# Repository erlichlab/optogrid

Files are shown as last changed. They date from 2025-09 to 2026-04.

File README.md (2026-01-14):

# OptoGrid

OptoGrid is a battery-powered BLE-enabled low-cost wireless random access optogenetic stimulation device, with 9-axis (acceleration XYZ, angular veleocity XYZ, magnetic field XYZ) movement tracking capability. 

## Specification

### Weight
| Component                | Weight (g) |
|--------------------------|------------|
| Battery PCB Assembly     | 0.9        |
| Main PCB Assembly        | 0.5        |
| Housing units + magnets  | 1.0        |
| **Total weight**         | **2.4**    |

### Battery link
https://www.aliexpress.com/item/1005007806295703.html?spm=a2g0o.order_list.order_list_main.10.24551802WD2qNq

## Folder Structure

- **3D/**  
  CAD models and mechanical assemblies for OptoGrid.

- **PCB/**  
  Original PCB project file (.eprj) exported from JLCEDA Pro, a folder containing PCB design files exported to Altium Designer format, PDF of the schematics, and exported PCBA production files.
- **OptoGrid_Photos.pdf/**  
  Photos of OptoGrid V0.05 assembly.
- **Assembly_SOP_V1.pdf/**  
  Protocl to reproduce OptoGrid V0.05 assembly.

## Purpose

This repository is to share the hardware design files of OptoGrid with OpenEphys. Its license is set to "All Rights Reserved" for now until device distribution begins.

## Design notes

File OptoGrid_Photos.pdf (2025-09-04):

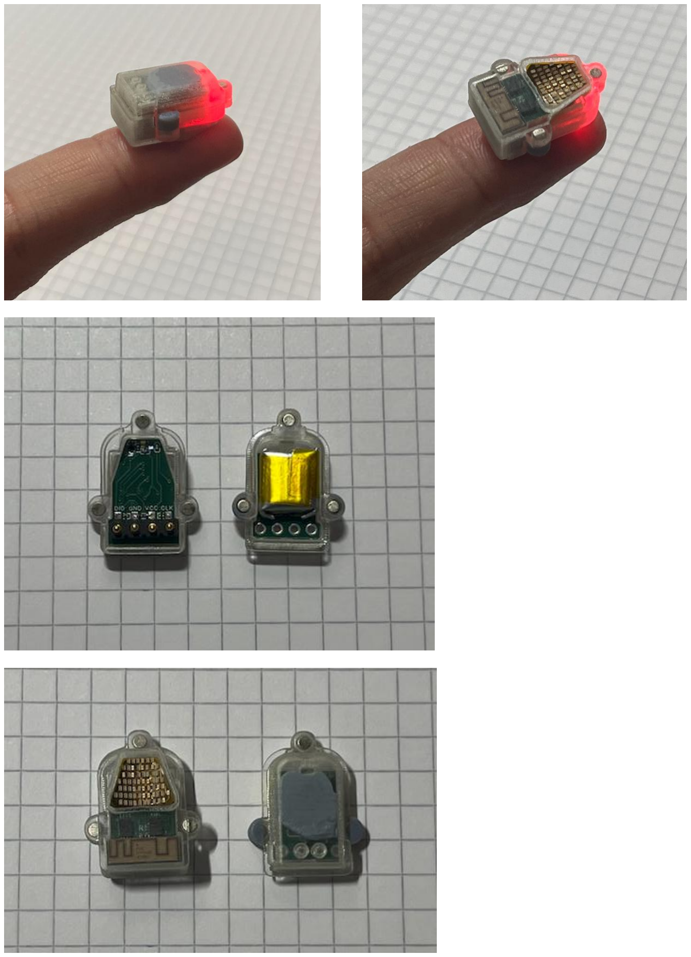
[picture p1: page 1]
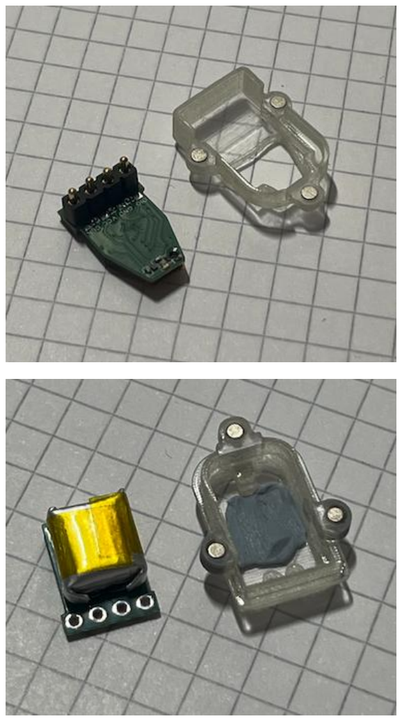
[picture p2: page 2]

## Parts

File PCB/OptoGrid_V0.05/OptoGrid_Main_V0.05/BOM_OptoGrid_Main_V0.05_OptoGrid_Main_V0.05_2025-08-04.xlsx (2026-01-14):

No. | Quantity | Comment | Designator | Footprint | Value | Manufacturer Part | Manufacturer | Supplier Part | Supplier | Name
1 | 2 | 2.2uF | C46,C54 | C0201 | 2.2uF | GRM033R61A225KE47D | muRata(村田) | C335106 | LCSC | 2.2uF
2 | 4 | Test-Point | CLK,DIO,GND,VCC | Test-Point-0.5mm
3 | 1 | YXT-BB10-16S-02 | CN1 | CONN-SMD_YXT-BB10-16S-02 |  | YXT-BB10-16S-02 | YXT(益鑫通） | C2763964 | LCSC | YXT-BB10-16S-02
4 | 1 | 811-22-004-30-002101 | J1 | 811-22-004-30-002101 |  | 811-22-004-30-002101 | Mill-Max | C29643123 | LC
5 | 1 | 220Ω | R2 | R0201 | 220Ω | RC0201FR-07220RL | YAGEO(国巨) | C274342 | LCSC | 220Ω
6 | 2 | 4.7kΩ | R4,R9 | R0201 | 4.7kΩ | AF0201FR-074K7L | YAGEO(国巨) | C2105831 | LCSC | 4.7kΩ
7 | 1 | 71.5Ω | R5 | R0201 | 71.5Ω | 0201WMF715JTEE | UNI-ROYAL(厚声) | C423441 | LCSC | 71.5Ω
8 | 1 | 82Ω | R6 | R0201 | 82Ω | RC-01W82R0FT | FH | C321062 | LCSC | 82Ω
9 | 2 | 1MΩ | R7,R8 | R0201 | 1MΩ | RC0201FR-071ML | YAGEO(国巨) | C295786 | LCSC | 1MΩ
10 | 1 | RED LED | U3 | BLUE_LED_KINGBRIGHT_0201 |  | APG0603SURC-TT | Kingbright | C5356830 | LCSC | RED LED
11 | 1 | HY0020 | U5 | HY0020_footprint_NoFilling
12 | 2 | TMUX1208RSVR | U6,U11 | UTQFN-16_L2.6-W1.8-P0.40-BL |  | TMUX1208RSVR | TI(德州仪器) | C2673274 | LCSC | TMUX1208RSVR
13 | 1 | NCP163AFCT330T2G | U7 | WLCSP-4_L0.6-W0.6-P0.35-R2-C2-TL |  | NCP163AFCT330T2G | onsemi(安森美) | C603648 | LCSC | NCP163AFCT330T2G
14 | 1 | BLUE LED | U12 | BLUE_LED_KINGBRIGHT_0201 |  | APG0603VBC-A1-5MAV | Kingbright | C5846953 | LCSC | BLUE LED

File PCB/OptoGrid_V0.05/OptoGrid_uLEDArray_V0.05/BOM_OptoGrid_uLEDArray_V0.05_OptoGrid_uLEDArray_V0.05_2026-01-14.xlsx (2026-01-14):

No. | Quantity | Comment | Designator | Footprint | Value | Manufacturer Part | Manufacturer | Supplier Part | Supplier | Name
1 | 1 | YXT-BB10-16P-02 | CN1 | CONN-SMD_YXT-BB10-16P-02 |  | YXT-BB10-16P-02 | YXT(益鑫通） | C2763972 | LCSC | YXT-BB10-16P-02
2 | 64 | BLUE LED | U1,U29,U30,U31,U32,U33,U34,U35,U36,U38,U39,U40,U41,U42,U43,U44,U45,U47,U48,U49,U50,U51,U52,U53,U54,U56,U57,U58,U59,U60,U61,U62,U63,U66,U67,U68,U69,U70,U71,U72,U73,U74,U75,U76,U77,U78,U79,U80,U81,U83,U84,U85,U86,U87,U88,U89,U90,U92,U93,U94,U96,U97,U98,U99 | BLUE_LED_KINGBRIGHT_0201 |  | XL-0201UBC (Brightness Grading D5) | XINGLIGHT | C3646921 | LCSC | BLUE LED

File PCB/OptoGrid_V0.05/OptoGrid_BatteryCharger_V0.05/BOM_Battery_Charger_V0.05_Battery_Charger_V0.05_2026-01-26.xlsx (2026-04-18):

No. | Quantity | Comment | Designator | Footprint | Value | Manufacturer Part | Manufacturer | Supplier Part | Supplier | Name
1 | 12 | 10uF | C1,C2,C3,C4,C5,C6,C7,C8,C9,C10,C11,C12 | C0603 | 10uF | CL10A106MA8NRNC | SAMSUNG(三星) | C96446 | LCSC | 10uF
2 | 6 | 811-22-002-30-001101 | J7,J8,J9,J10,J11,J12 | MilMax_2Pin_2.54mmPitch_4.49mmTall_SMT |  |  |  |  |  | 811-22-002-30-001101
3 | 6 | 44.2kΩ | R2,R27,R28,R29,R30,R31 | R0603 | 44.2kΩ | 0603WAF4422T5E | UNI-ROYAL(厚声) | C23056 | LCSC | 44.2kΩ
4 | 6 | 1kΩ | R3,R7,R10,R13,R16,R19 | R0603 | 1kΩ | 0603WAF1001T5E | UNI-ROYAL(厚声) | C21190 | LCSC | 1kΩ
5 | 2 | 5.1kΩ | R4,R5 | R0603 | 5.1kΩ | 0603WAF5101T5E | UNI-ROYAL(厚声) | C23186 | LCSC | 5.1kΩ
6 | 6 | 2kΩ | R21,R22,R23,R24,R25,R26 | R0603 | 2kΩ | 0603WAF2001T5E | UNI-ROYAL(厚声) | C22975 | LCSC | 2kΩ
7 | 6 | TP4056-MS | U1,U3,U5,U7,U9,U11 | SOP-8_L4.9-W3.9-P1.27-LS6.0-TL-EP |  | TP4056-MS | MSKSEMI(美森科) | C7473158 | LCSC | TP4056-MS
8 | 6 | XL-1608SURUGC | U2,U4,U6,U8,U10,U12 | LED-SMD_4P-L1.6-W0.8-RD_1 |  | XL-1608SURUGC | XINGLIGHT(成兴光) | C5349934 | LCSC | XL-1608SURUGC
9 | 2 | TYPE-C 6P(073) | USB1,USB2 | TYPE-C-SMD_TYPE-C-6P_5 |  | TYPE-C 6P(073) | SHOU HAN(首韩) | C668623 | LCSC | TYPE-C 6P(073)

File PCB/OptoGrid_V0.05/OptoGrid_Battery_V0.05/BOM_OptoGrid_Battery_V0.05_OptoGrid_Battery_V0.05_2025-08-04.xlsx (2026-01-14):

No. | Quantity | Comment | Designator | Footprint | Value | Manufacturer Part | Manufacturer | Supplier Part | Supplier | Name
1 | 3 | 2.2uF | C46,C48,C54 | C0201 | 2.2uF | GRM033R61A225KE47D | muRata(村田) | C335106 | LCSC | 2.2uF
2 | 1 | 10nF | C49 | C0201 | 10nF | GRM033R71A103KA01D | muRata(村田) | C76941 | LCSC | 10nF
3 | 1 | 100nF | C50 | C0201 | 100nF | GRM033Z71A104KE14D | muRata(村田) | C161494 | LCSC | 100nF
4 | 1 | 100nF | C55 | C0201 | 100nF | GRM033R61E104KE14D | muRata(村田) | C76939 | LCSC | 100nF
5 | 1 | 10uF | C57 | C0402 | 10uF | CL05A106MP5NUNC | SAMSUNG(三星) | C315248 | LCSC | 10uF
6 | 1 | 220nF | C60 | C0201 | 220nF | GRM033R61E224KE01D | muRata(村田) | C701263 | LCSC | 220nF
7 | 1 | 2.2uF | C61 | C0402 | 2.2uF | GRM155Z71A225KE01D | muRata(村田) | C2997286 | LCSC | 2.2uF
8 | 1 | BAT30F4 | D1 | DFN0603-D_L0.6-W0.3-P0.34-RD |  | BAT30F4 | ST(意法半导体) | C314018 | LCSC | BAT30F4
9 | 1 | 510Ω | R3 | R0201 | 510Ω | RC0201FR-07510RL | YAGEO(国巨) | C57784 | LCSC | 510Ω
10 | 1 | DS6101AED4 | U2 | DFN-4_L1.0-W1.0-P0.65-BL-EP |  | DS6101AED4 | DSTECH(奥简科技) | C7499469 | LCSC | DS6101AED4
11 | 1 | NCP163AFCT330T2G | U7 | WLCSP-4_L0.6-W0.6-P0.35-R2-C2-TL |  | NCP163AFCT330T2G | onsemi(安森美) | C603648 | LCSC | NCP163AFCT330T2G
12 | 1 | LIS2MDLTR | U8 | LGA-12_L2.0-W2.0-P0.50-BL |  | LIS2MDLTR | ST(意法半导体) | C919695 | LCSC | LIS2MDLTR
13 | 1 | IIM-42652 | U9 | LGA-14_L3.0-W2.5-P0.50-TL |  | IIM-42652 | TDK InvenSense(应美盛) | C2988404 | LCSC | IIM-42652

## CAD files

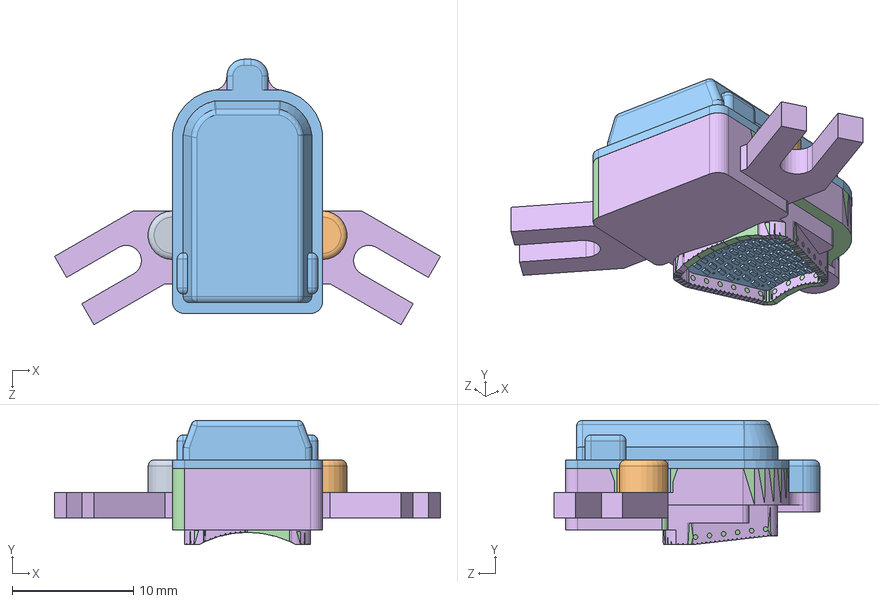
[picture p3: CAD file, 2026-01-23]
3D/OptoGrid_V0.051_Assembly.STEP
31.8 x 10.2 x 21.9 mm
2-UpperHousing_OptoGrid_V0.05_Battery
1-OptoGrid_LowerHousing_no_headfix
COMPOUND_2.step x 2
COMPOUND-0_2.step
COMPOUND-1_2.step x 7
COMPOUND-2_2.step
pPdb-Board.step
pPdb-U6-UTQFN-16_L2.6-W1.8-P0.40-BL.step x 2
B-Flex_uLEDMatrix
BOT_Mold_V0.04
HY0020
1B-OptoGrid_LowerHousing_headfix
Magnet_2mm1mm x 3
COMPOUND_1.step
COMPOUND-0_1.step
COMPOUND-1_1.step x 7
COMPOUND-2_1.step
COMPOUND-3_1.step
vdLQ-Board.step
vdLQ-U2-DFN-4_L1.0-W1.0-P0.65-BL-EP.step
vdLQ-C57-C0402.step x 2
vdLQ-D1-DFN0603-D_L0.6-W0.3-P0.34-RD.step
Battery_25mAh
Magnet_2mm2mm x 3

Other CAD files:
3D/OptoGrid_V0.051_Assembly.SLDASM

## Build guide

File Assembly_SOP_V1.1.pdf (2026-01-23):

## Procedure to assemble the OptoGrid device

Ver. | Author | Date | Note
1.0 | Fukui (Daniel) Yang, Sainsbury Wellcome Centre, UCL | 14/01/2026 | Initial Commit
1.1 | Fukui (Daniel) Yang | 23/01/2026 | Changed 3D model for head-fixed base plate; magnets from N42 to N52

## Table of content

## Step 1: Order Main PCBA, Battery PCBA, and uLED matrix

# Module 1: Printed Circuit Board and Assembly

## Step 1: Order Main PCBA, Battery PCBA, and uLED matrix PCBA

1. There are three PCBA components to the OptoGrid device, they can be ordered from commercial PCBA manufacturer with the production files and specification below:
| PCBA File Location | Recommended Manufacturer | PCB Production Specification
1 PCB/OptoGrid_V0.0 | 5/OptoGrid_Battery_ V0.05 | | PCB Thickness: 0.6mm Layer: 2 Layers Material: FR-4 Surface finish: HASL lead free Silkscreen: White Min hole size: 0.3mm diameter Min track/spacing:4/4mil Via process: Tenting vias Finished copper: 1 oz Cu Solder mask: Green
2 PCB/OptoGrid_V0.0 | 5/OptoGrid_Main_V 0.05
3 PCB/OptoGrid_V0.0 | 5/OptoGrid_uLEDAr ray_V0.05 | | PCB Type: Flexible PCB FPC Thickness: 0.1mm Layer: 2 Layers Material: Polyimide Flex Surface finish: Immersion gold (ENIG), 1U Silkscreen: None Min hole size: 0.15/0.35mm diameter Min track/spacing: ≥0.06mm Via process: N/A Finished copper: 1 oz Cu Solder mask: Yellow Coverlay
PCBWay | PCB Type: Standard PCB

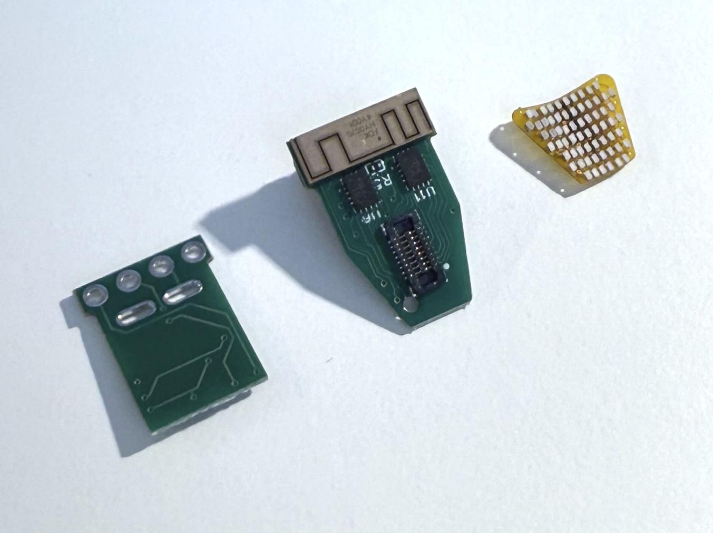
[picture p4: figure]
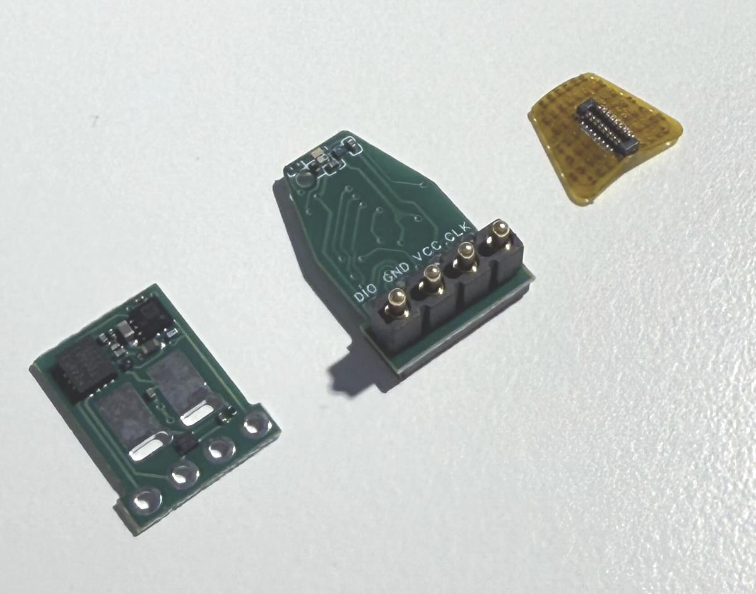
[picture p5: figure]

Figure 1: Photos of the three PCBA components that arrives from the manufacturer

## Step 2: Flash firmware onto the Main PCBA

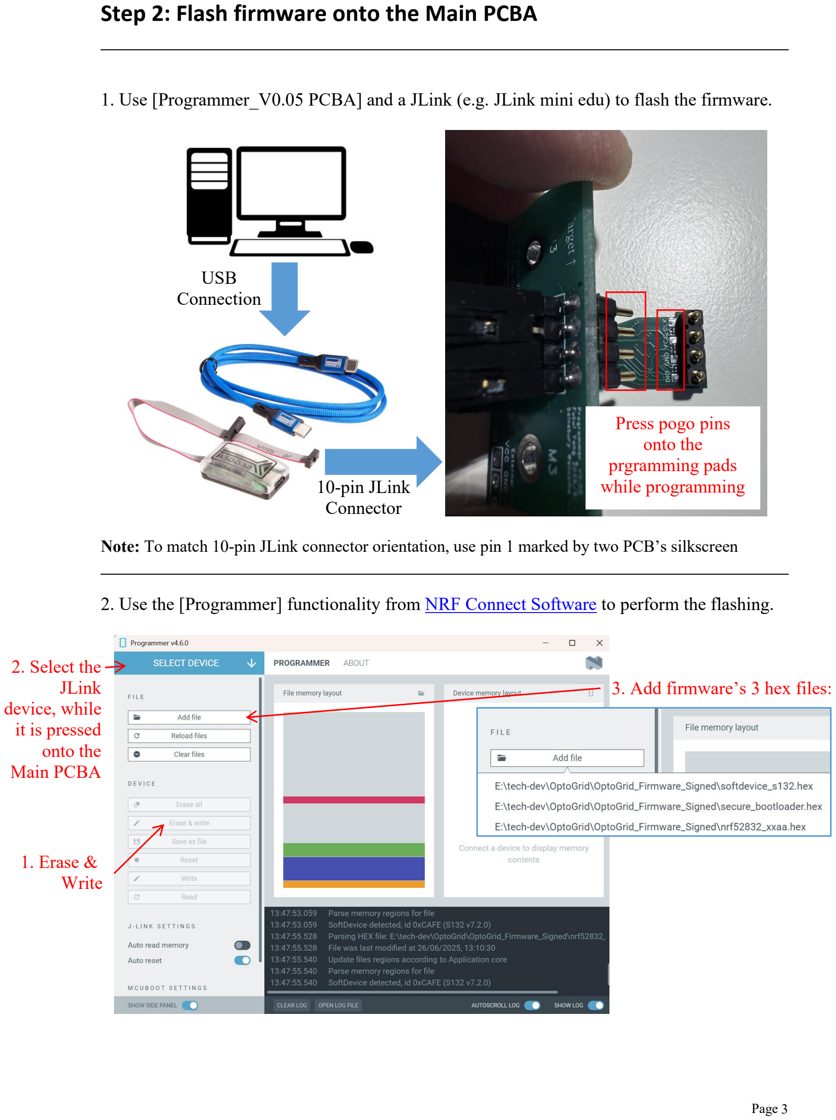
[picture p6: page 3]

1. Use [Programmer_V0.05 PCBA] and a JLink (e.g. JLink mini edu) to flash the firmware.

Note: To match 10-pin JLink connector orientation, use pin 1 marked by two PCB’s silkscreen

2. Use the [Programmer] functionality from NRF Connect Software (https://www.nordicsemi.com/Products/Development-tools/nRF-Connect-for-Desktop/Download) to perform the flashing.

USB
Connection

10-pin JLink
Connector

Press pogo pins
onto the
prgramming pads
while programming
3. Add firmware’s 3 hex files:
2. Select the
JLink
device, while
it is pressed
onto the
Main PCBA
1. Erase &
Write

## Step 3: Assemble the uLED matrix to the Main PCBA

1. Align the B2B connectors, and press them in

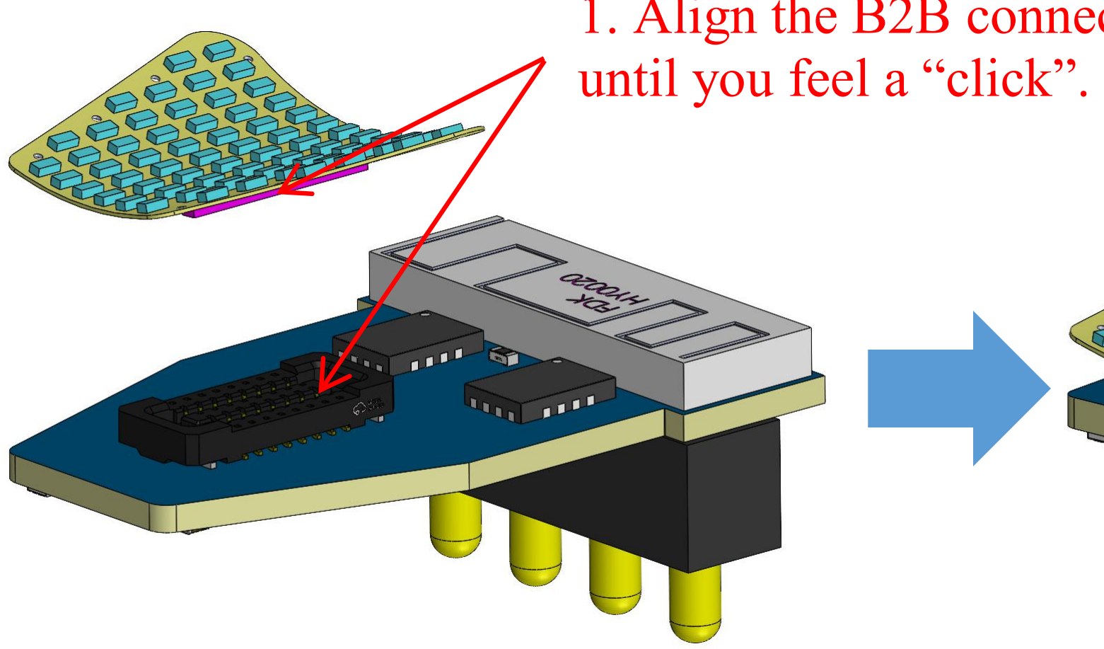
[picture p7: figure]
until you feel a “click”.
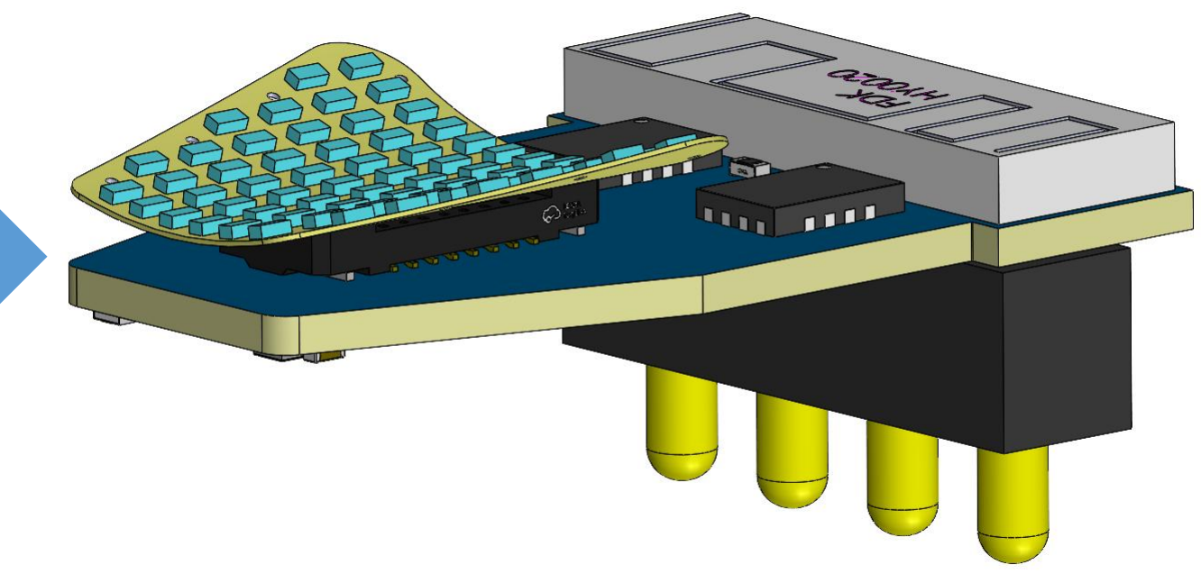
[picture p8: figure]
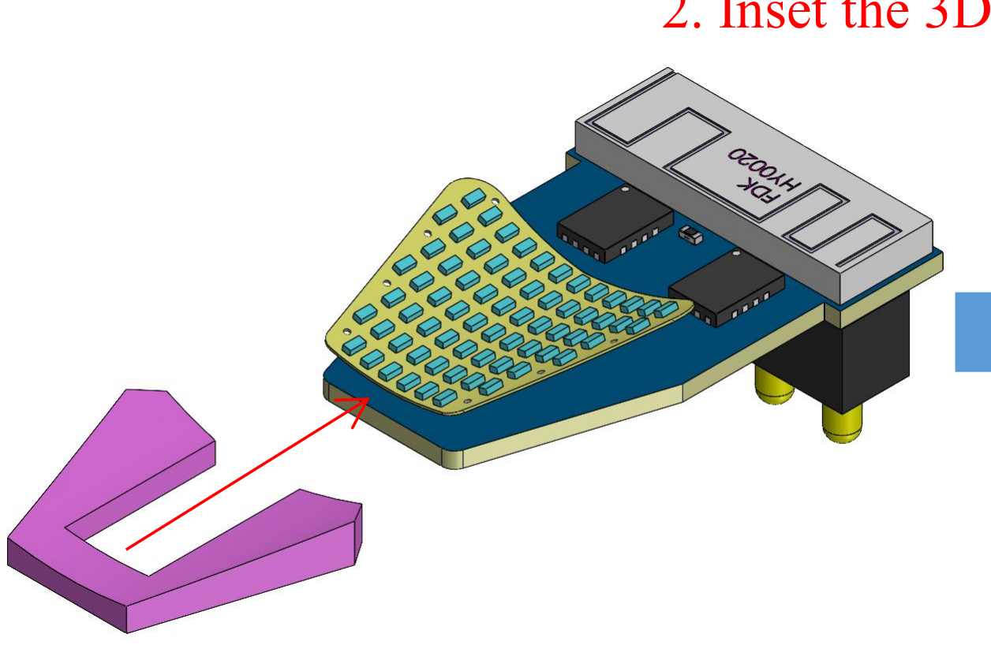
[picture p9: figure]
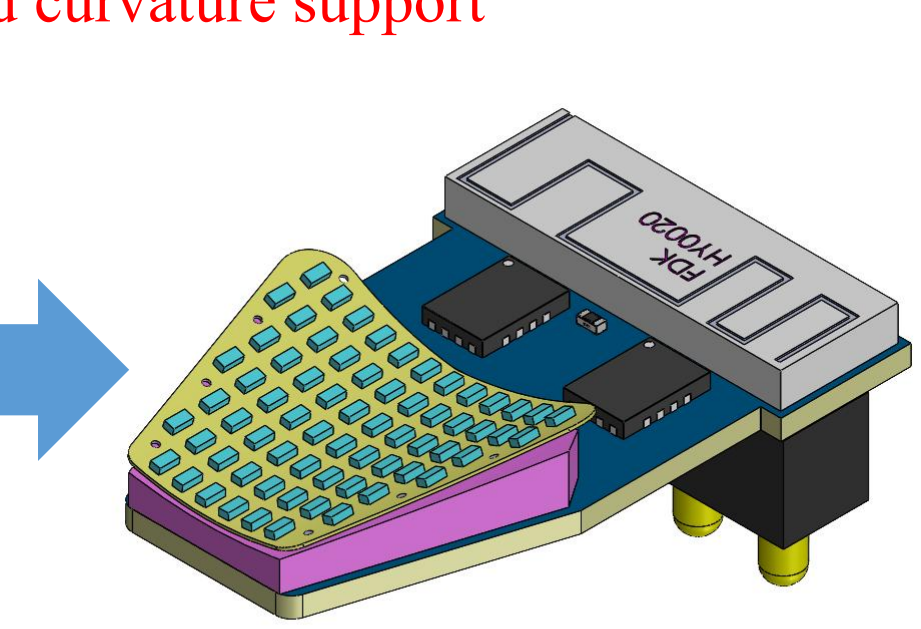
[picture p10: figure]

2. Inset the 3D-printed curvature support

## Step 4: Solder battery onto the battery PCBA

1. Flip the leads up to be perpendicular to the battery’s surface, and cut away access leads (part of the lead above dashed line) from the battery.

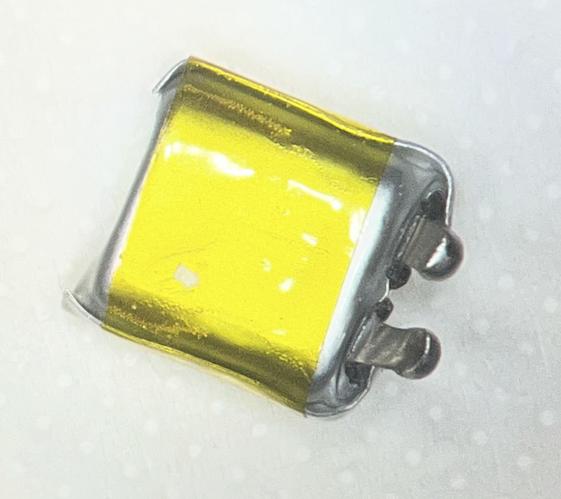
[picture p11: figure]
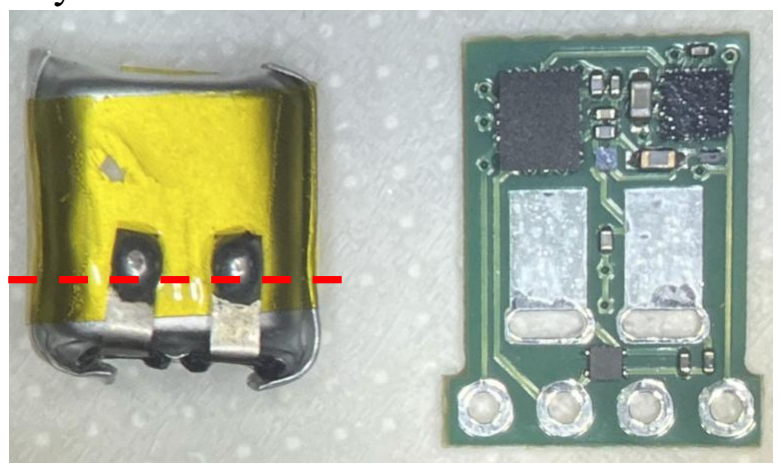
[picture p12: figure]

2. Insert the two leads through the holes on the PCBA, and flip the leads onto the solder pads, then solder the leads to the pads (solder tip temperature: 320 degree C )

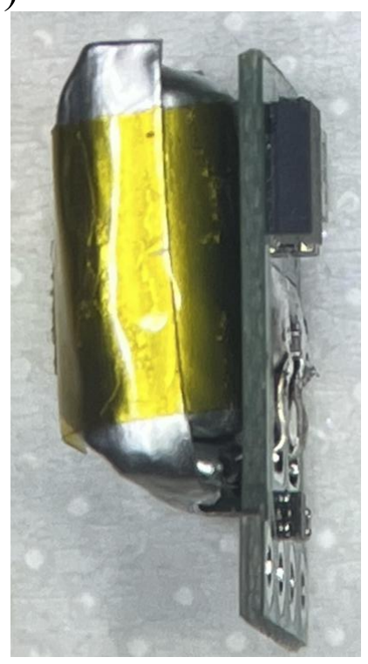
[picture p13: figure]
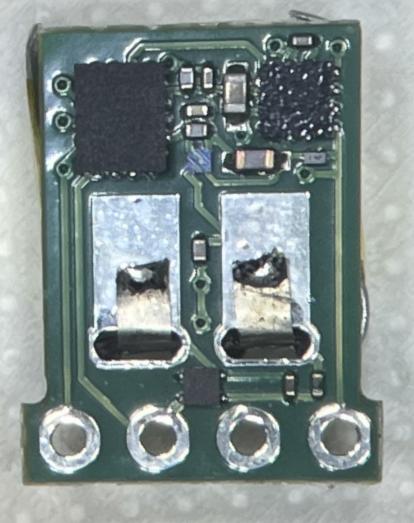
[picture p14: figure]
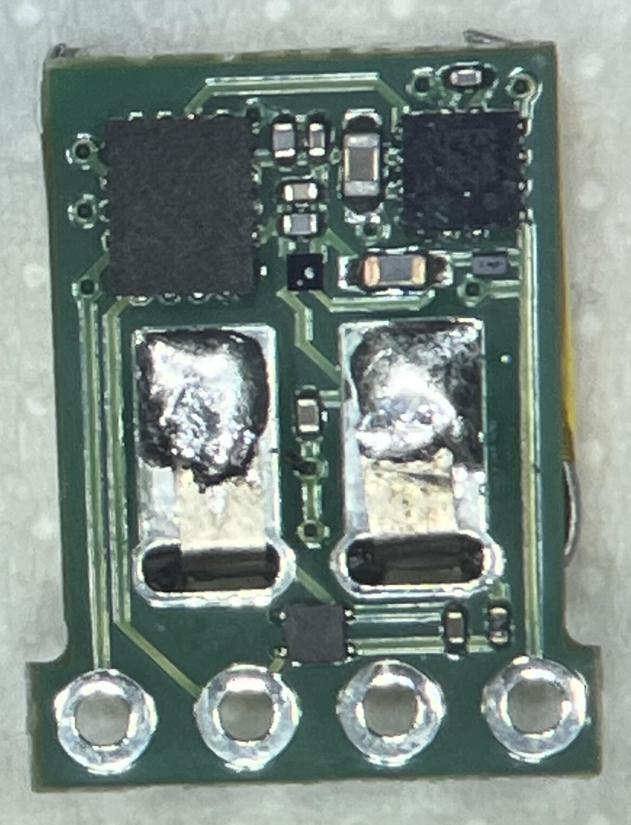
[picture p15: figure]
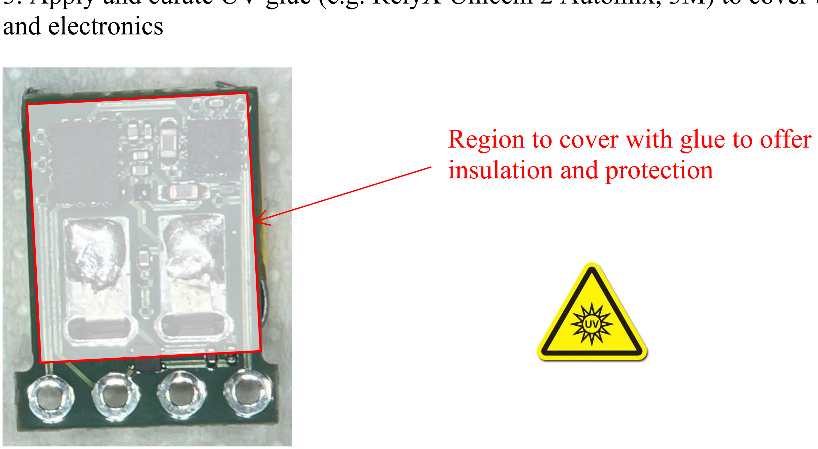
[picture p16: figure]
and electronics; Region to cover with glue to offer insulation and protection

3. Apply and curate UV glue (e.g. RelyX Unicem 2 Automix, 3M) to cover the solder points

# Module 2: Housing Unit Assembly

## Step 1: Order 3D printing of housing units

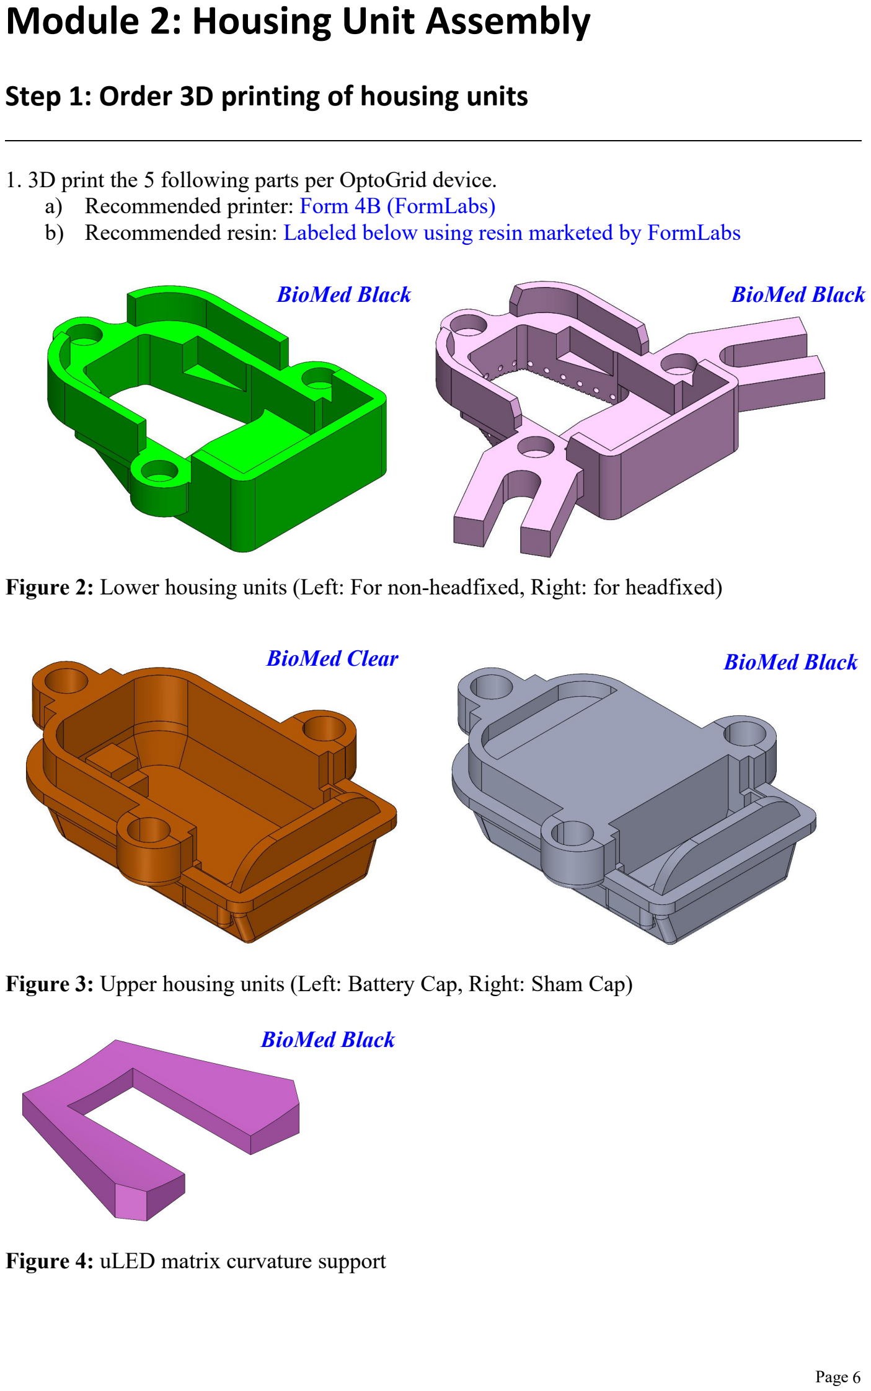
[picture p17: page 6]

1. 3D print the 5 following parts per OptoGrid device. a) Recommended printer: Form 4B (FormLabs)
b) Recommended resin: Labeled below using resin marketed by FormLabs

Figure 2: Lower housing units (Left: For non-headfixed, Right: for headfixed)

Figure 3: Upper housing units (Left: Battery Cap, Right: Sham Cap)

Figure 4: uLED matrix curvature support

BioMed Black | BioMed Black
BioMed Clear | BioMed Black

BioMed Black

## Step 2: Glue magnets to the housing units

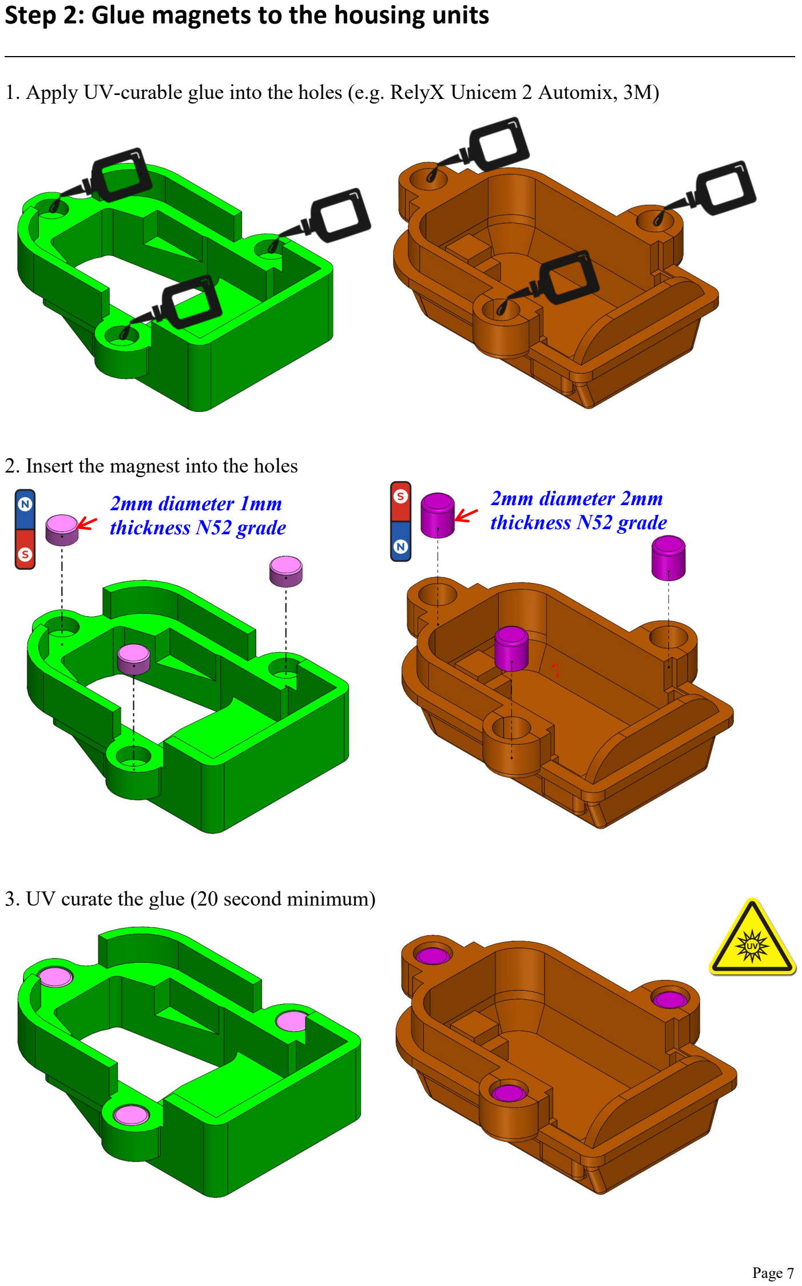
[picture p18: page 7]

1. Apply UV-curable glue into the holes (e.g. RelyX Unicem 2 Automix, 3M)
2. Insert the magnest into the holes
3. UV curate the glue (20 second minimum)

2mm diameter 1mm
thickness N52 grade

2mm diameter 2mm
thickness N52 grade

## Step 3: Test assembly of the PCBA with the housing units

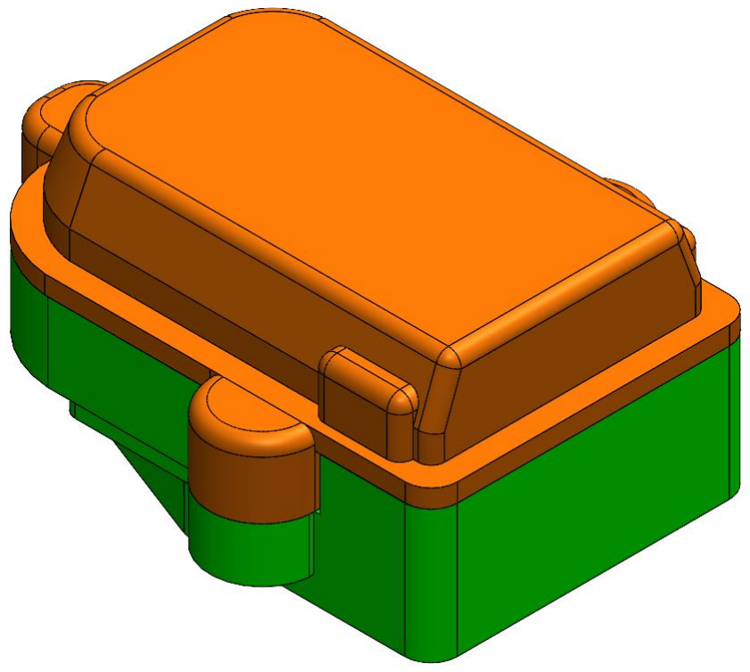
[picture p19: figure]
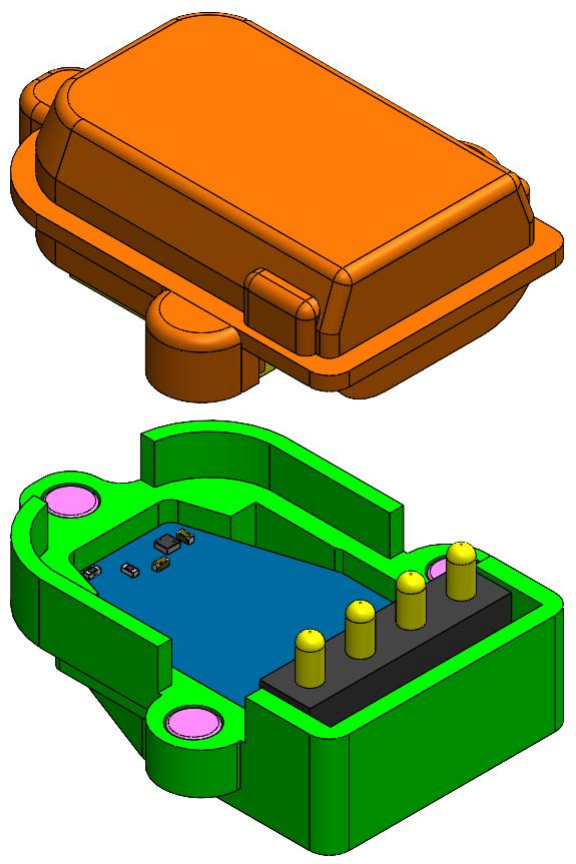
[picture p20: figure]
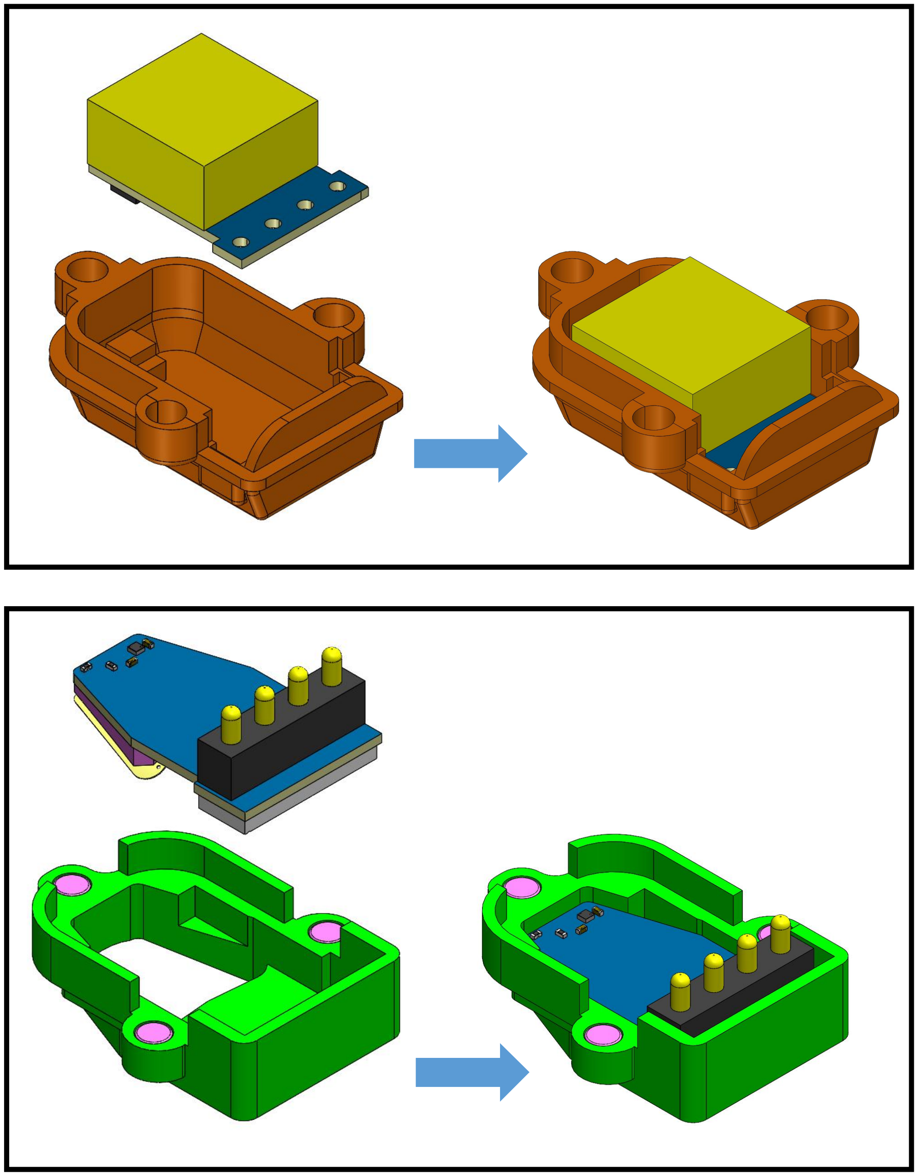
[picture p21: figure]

# Module 3: Software Deployment

1. Please refer to this GitHub repository for deployment of the PC software that interfaces with the OptoGrid device. https://github.com/danielfrankch/optogrid-pc-app
2. Quick guide on how to use the web-based GUI to interact with the OptoGrid device.

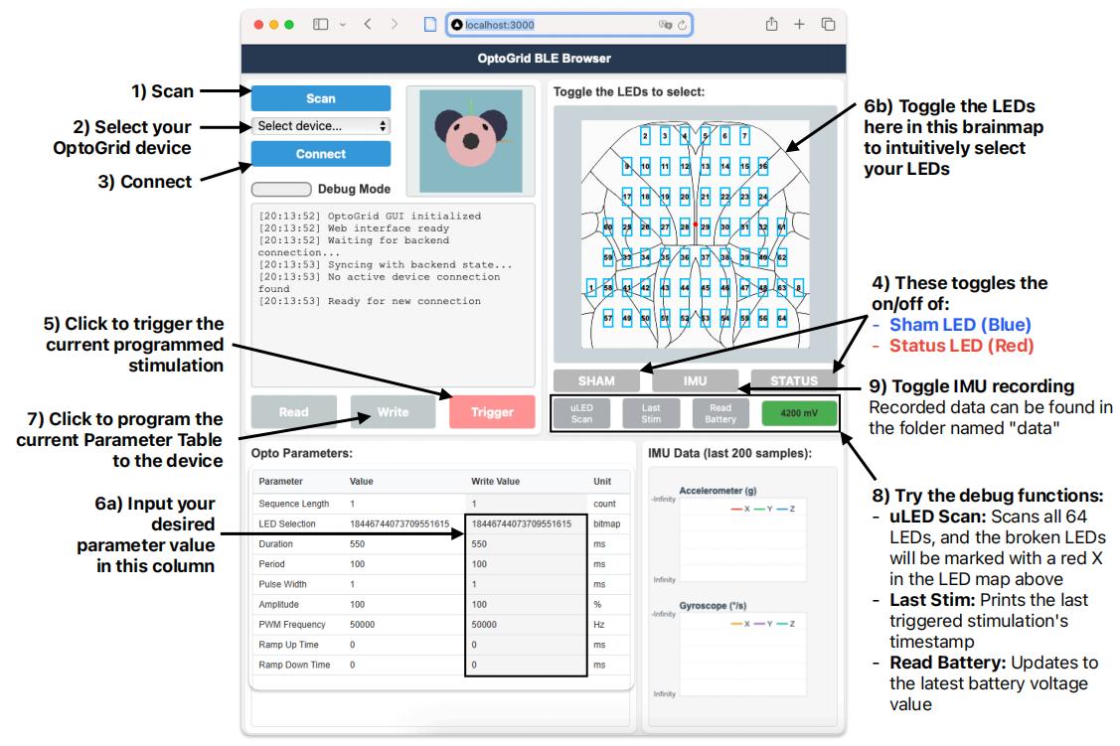
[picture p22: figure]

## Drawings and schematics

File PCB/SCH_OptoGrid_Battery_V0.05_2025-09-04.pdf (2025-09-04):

# 6-axis IMU Battery protection

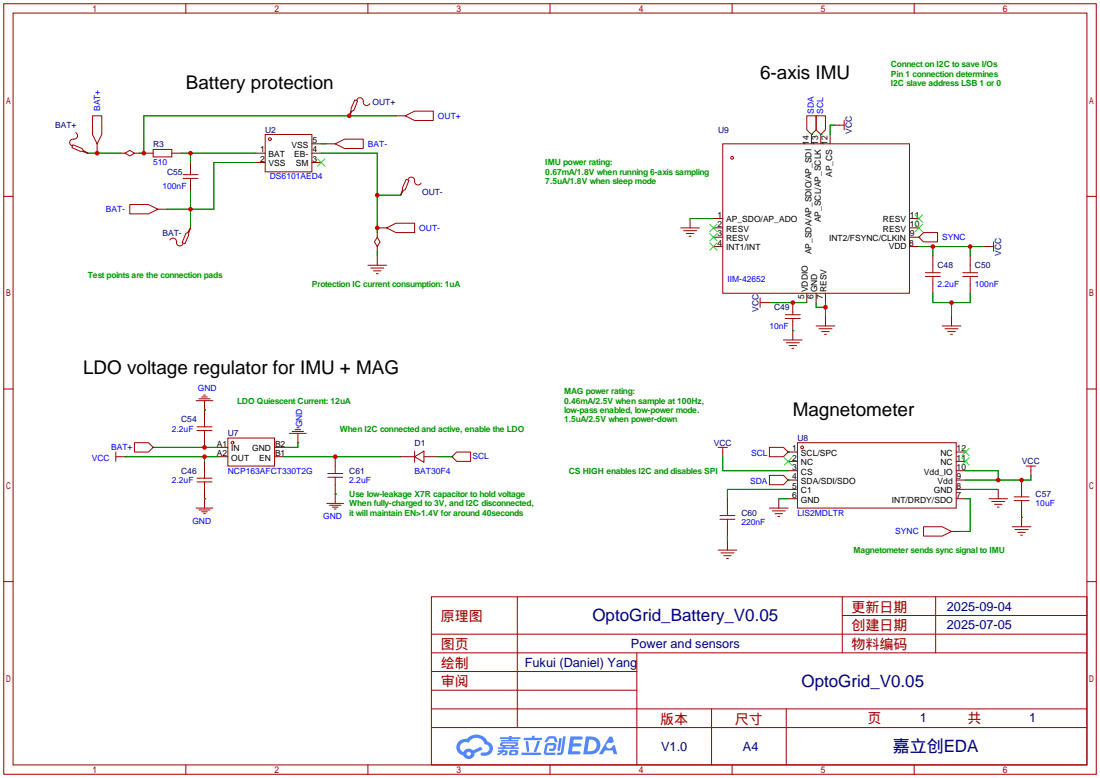
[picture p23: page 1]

Connect on I2C to save I/Os
Pin 1 connection determines
I2C slave address LSB 1 or 0

IMU power rating:
0.67mA/1.8V when running 6-axis sampling
7.5uA/1.8V when sleep mode

Test points are the connection pads

Protection IC current consumption: 1uA

LDO voltage regulator for IMU + MAG

MAG power rating:
0.46mA/2.5V when sample at 100Hz,
low-pass enabled, low-power mode.
1.5uA/2.5V when power-down

When I2C connected and active, enable the LDO

Use low-leakage X7R capacitor to hold voltage
When fully-charged to 3V, and I2C disconnected,
it will maintain EN>1.4V for around 40seconds
GND

CS HIGH enables I2C and disables SPI

Magnetometer sends sync signal to IMU

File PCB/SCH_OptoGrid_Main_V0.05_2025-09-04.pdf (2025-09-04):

I2C Pull-up | B2B Connector to uLED matrix

# BLE Chip

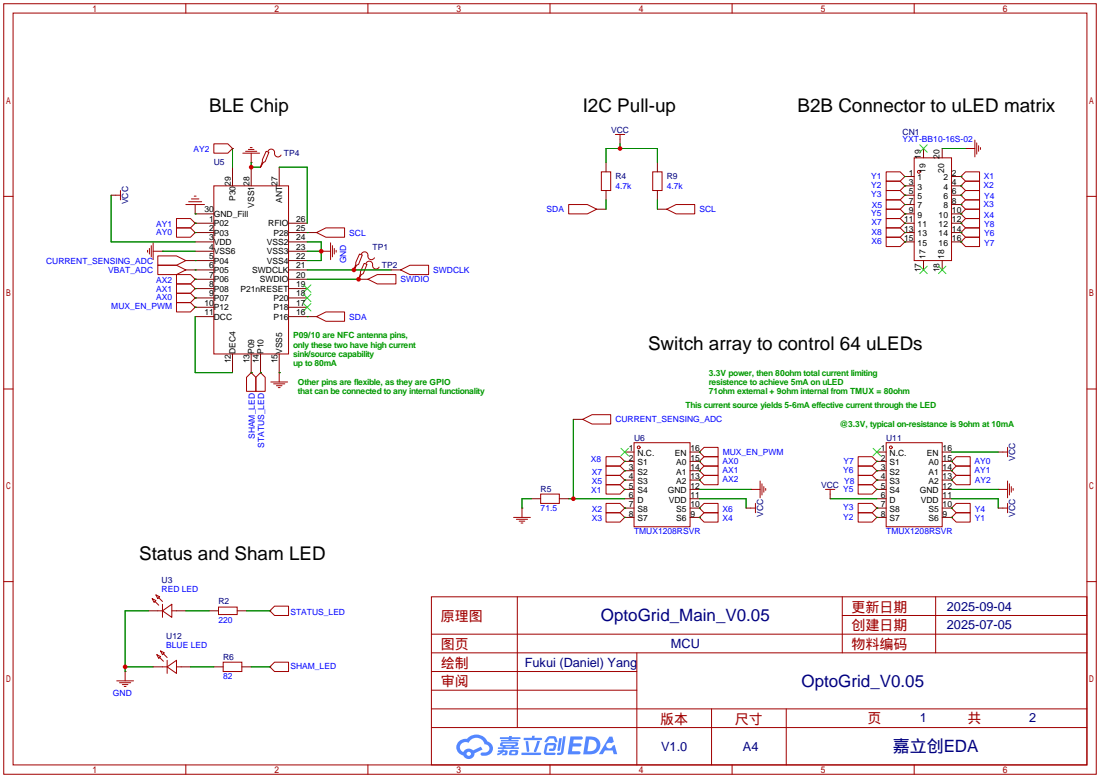
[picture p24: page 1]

P09/10 are NFC antenna pins,
only these two have high current
sink/source capability
Other pins are flexible, as they are GPIO
that can be connected to any internal functionality

Switch array to control 64 uLEDs

3.3V power, then 80ohm total current limiting
resistence to achieve 5mA on uLED
71ohm external + 9ohm internal from TMUX = 80ohm
This current source yields 5-6mA effective current through the LED
S5 10 VDD 11 GND 12 A2 13 A1 14 A0 15 EN 16

@3.3V, typical on-resistance is 9ohm at 10mA

Status and Sham LED

# Spring-loaded connector to receive unregulated power from BatteryPCB Battery range: 3.5~4.2V Battery capacity: 25mAh

VCC

GND

GND

# LDO voltage regulator

C46
2.2uF

IN A1

OUT A2 EN B1 GND B2

U7

NCP163AFCT330T2G

BAT+
BAT+

C54
2.2uF

GND

BAT+

R7
1M

R8
1M

VBAT_ADC

BAT+

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
# Battery voltage sensing

TP3

## @4.2V input, LDO efficiency ~= 3.3/4.2 = 78.6%

## If using Buck DC-DC regulator, the efficiency could be increased to 90~95%, but even the smallest DC-DC chip occupies 2mm x 2mm of space (compared to the 0.6mm x 0.6mm LDO chip). And DC-DC would need

additional components as well (inductor/capacitor).

## DC-DC cannot fit on this PCBA, while providing just

11%~16% increase in efficiency.

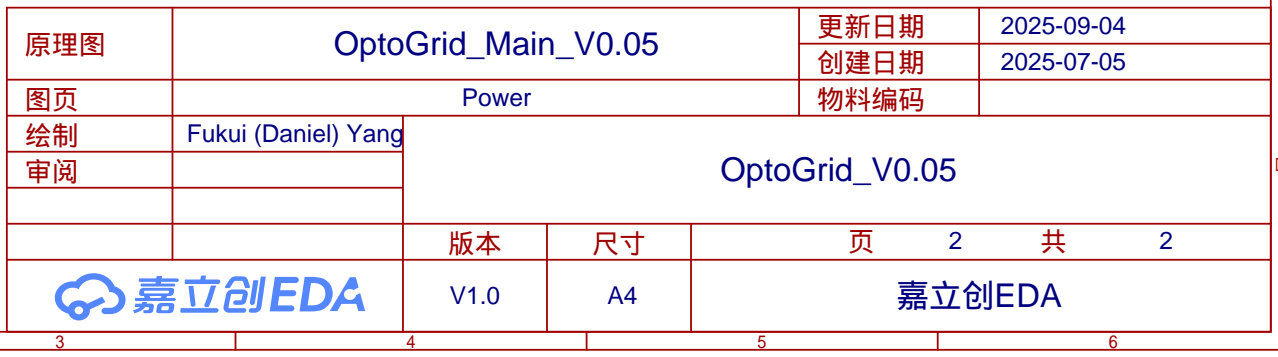
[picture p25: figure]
嘉立创EDA; Fukui (Daniel) Yang; OptoGrid_V0.05; 2025-09-04 2025-07-05 OptoGrid_Main_V0.05; Power; 创建日期 物料编码; 原理图; 更新日期

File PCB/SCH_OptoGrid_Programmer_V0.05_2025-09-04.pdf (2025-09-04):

# Connect 4pin header to 4pin pogo-pin

# Header for external 3.3V

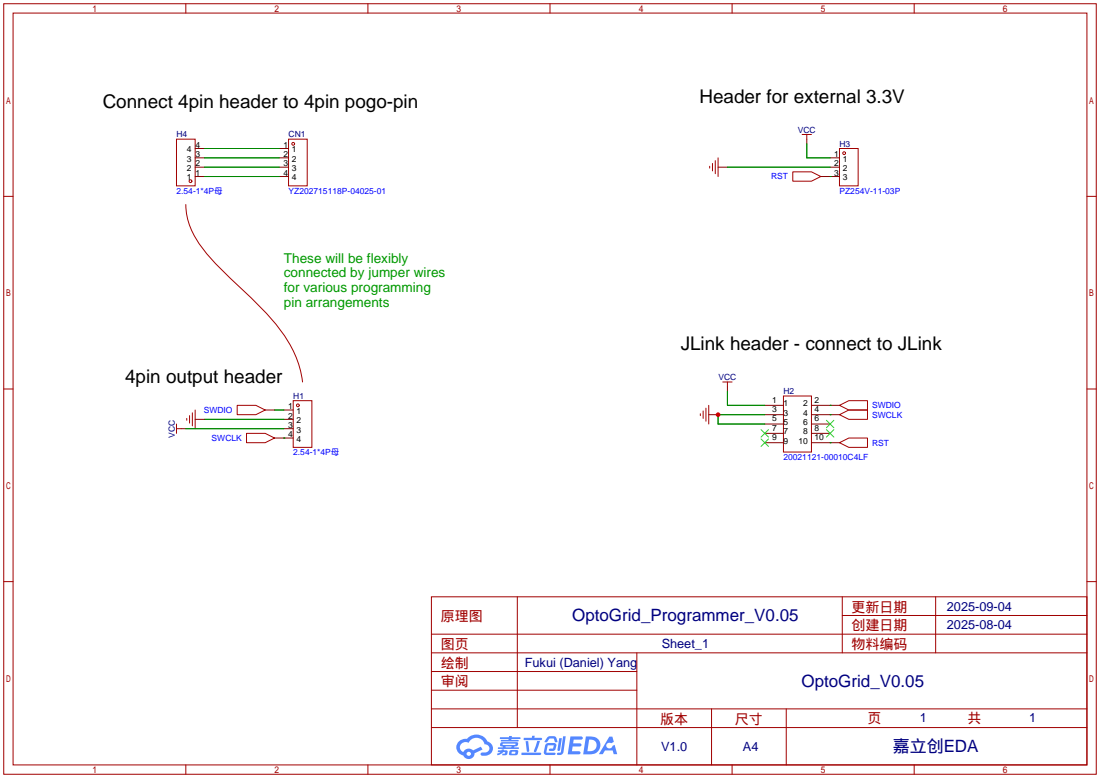
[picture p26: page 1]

These will be flexibly
connected by jumper wires
for various programming
pin arrangements

JLink header - connect to JLink

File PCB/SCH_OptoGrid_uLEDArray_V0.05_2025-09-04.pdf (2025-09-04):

# 64 LEDs, the actual LEDs assembled is managed by BOM

## Green 0201 LED - APG0603CGC-TT or APG0603ZGC-5MAV

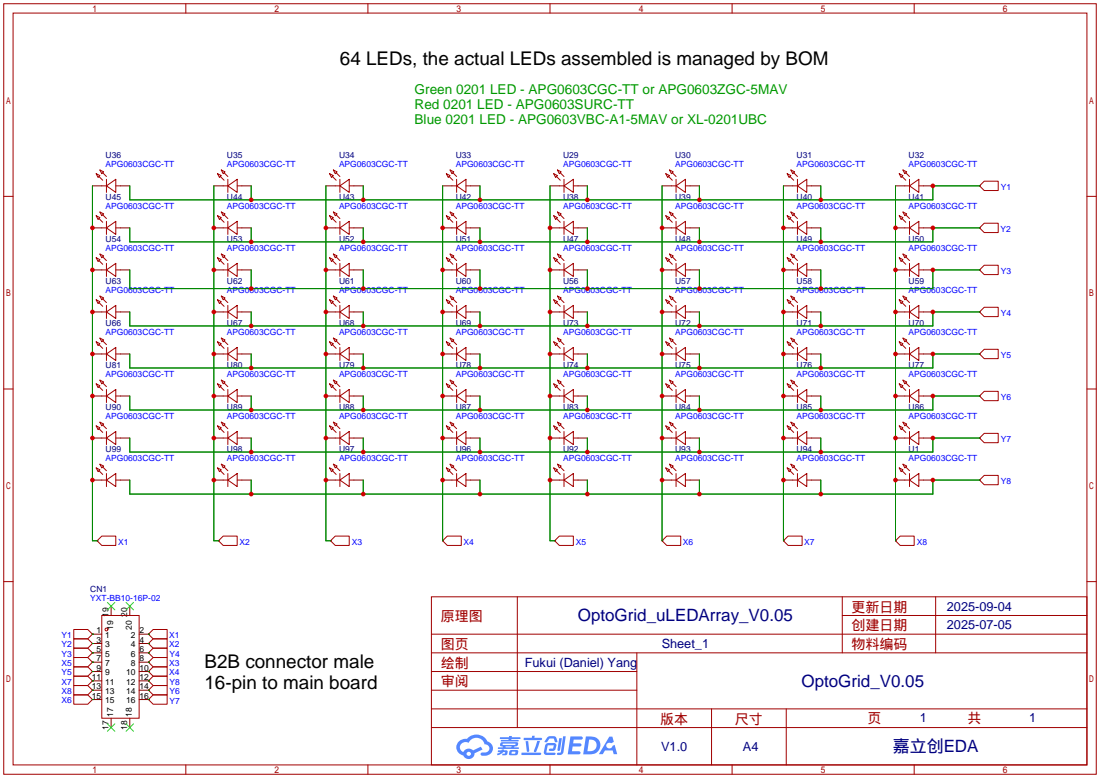
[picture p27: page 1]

Red 0201 LED - APG0603SURC-TT
Blue 0201 LED - APG0603VBC-A1-5MAV or XL-0201UBC

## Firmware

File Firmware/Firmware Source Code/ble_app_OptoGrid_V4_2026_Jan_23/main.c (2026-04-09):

/**
 * Copyright (c) 2017 - 2021, Nordic Semiconductor ASA
 *
 * All rights reserved.
 *
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
 * 3. Neither the name of Nordic Semiconductor ASA nor the names of its
 *    contributors may be used to endorse or promote products derived from this
 *    software without specific prior written permission.
 *
 * 4. This software, with or without modification, must only be used with a
 *    Nordic Semiconductor ASA integrated circuit.
 *
 * 5. Any software provided in binary form under this license must not be reverse
 *    engineered, decompiled, modified and/or disassembled.
 *
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
 */

/** @brief GATT Service server example application main file with DFU support.

    @details This file contains the main source code for OptoGrid application that includes:
             - GATT Server Peripheral functionality for nRF52832
             - PWM control for LED amplitude modulation
             - Ramp up/down functionality for smooth amplitude transitions
             - Secure DFU Buttonless Service for firmware updates
             - I2C device support (IMU + MAG sensors)
*/
// Include headers for used modules
#include <stdint.h>
#include <stdio.h>
#include <string.h>
#include <stdarg.h>
#include "nordic_common.h"
#include "nrf_sdm.h"
#include "ble.h"
#include "ble_hci.h"
#include "ble_srv_common.h"
#include "nrf_sdh.h"
#include "nrf_sdh_ble.h"
#include "nrf_sdh_soc.h"
#include "app_util.h"
#include "app_error.h"
#include "app_timer.h"
#include "bsp_btn_ble.h"
#include "peer_manager.h"
#include "peer_manager_handler.h"
#include "nrf_ble_gatt.h"
#include "nrf_drv_timer.h"
#include "nrf_drv_pwm.h"
#include "nrf_pwr_mgmt.h"
#include "nrf_log.h"
#include "nrf_log_ctrl.h"
#include "nrf_log_default_backends.h"
#include "ble_advdata.h"
#include "ble_advertising.h"
#include "ble_conn_params.h"
#include "ble_conn_state.h"
#include "nrf_drv_twi.h"
#include "app_util_platform.h"
#include "fds.h"
#include "nrf_drv_clock.h"
#include "nrf_power.h"
#include "nrf_bootloader_info.h"
#include "nrf_delay.h"
#include "nrf_drv_saadc.h"
#include "nrfx_wdt.h"

// Direct Firmware Update (DFU) includes
#include "nrf_dfu_ble_svci_bond_sharing.h"
#include "nrf_svci_async_function.h"
#include "nrf_svci_async_handler.h"
#include "ble_dfu.h"

#define APP_BLE_CONN_CFG_TAG      1
#define APP_BLE_OBSERVER_PRIO     3
#define APP_SOC_OBSERVER_PRIO     1
#define DEVICE_NAME                     "JON-O-0001"                                /**< Name of device. Will be included in the advertising data. */
#define APP_ADV_INTERVAL                300                                         /**< The advertising interval (in units of 0.625 ms. This value corresponds to 187.5 ms). */
#define APP_ADV_DURATION                0                                           /**< The advertising duration (180 seconds) in units of 10 milliseconds. */

#define MIN_CONN_INTERVAL               MSEC_TO_UNITS(7.5, UNIT_1_25_MS)            /**< Minimum acceptable connection interval (0.1 seconds). */
#define MAX_CONN_INTERVAL               MSEC_TO_UNITS(7.5, UNIT_1_25_MS)            /**< Maximum acceptable connection interval (0.2 second). */
#define SLAVE_LATENCY                   0                                           /**< Slave latency. */
#define CONN_SUP_TIMEOUT                MSEC_TO_UNITS(4000, UNIT_10_MS)             /**< Connection supervisory timeout (4 seconds). */

#define FIRST_CONN_PARAMS_UPDATE_DELAY  APP_TIMER_TICKS(5000)                       /**< Time from initiating event (connect or start of notification) to first time sd_ble_gap_conn_param_update is called (5 seconds). */
#define NEXT_CONN_PARAMS_UPDATE_DELAY   APP_TIMER_TICKS(30000)                      /**< Time between each call to sd_ble_gap_conn_param_update after the first call (30 seconds). */
#define MAX_CONN_PARAMS_UPDATE_COUNT    3                                           /**< Number of attempts before giving up the connection parameter negotiation. */

#define SEC_PARAM_BOND                  1                                           /**< Perform bonding. */
#define SEC_PARAM_MITM                  0                                           /**< Man In The Middle protection not required. */
#define SEC_PARAM_LESC                  0                                           /**< LE Secure Connections not enabled. */
#define SEC_PARAM_KEYPRESS              0                                           /**< Keypress notifications not enabled. */
#define SEC_PARAM_IO_CAPABILITIES       BLE_GAP_IO_CAPS_NONE                        /**< No I/O capabilities. */
#define SEC_PARAM_OOB                   0                                           /**< Out Of Band data not available. */
#define SEC_PARAM_MIN_KEY_SIZE          7                                           /**< Minimum encryption key size. */
#define SEC_PARAM_MAX_KEY_SIZE          16                                          /**< Maximum encryption key size. */

#define DEAD_BEEF                       0xDEADBEEF                                  /**< Value used as error code on stack dump, can be used to identify stack location on stack unwind. */

// LED Control Pin Definitions
#define STATUS_LED_PIN      10
#define SHAM_LED_PIN        9
#define STIM_LED_ENABLE_PIN 12

// Charlie-plexing pins for 64 LED array
#define AX0_PIN             7  // Column select bit 0
#define AX1_PIN             8   // Column select bit 1  
#define AX2_PIN             6   // Column select bit 2
#define AY0_PIN             3   // Row select bit 0
#define AY1_PIN             2   // Row select bit 1
#define AY2_PIN             30  // Row select bit 2


#define LOG_BUFFER_SIZE 72
#define MAX_LOG_LENGTH 128

// Track global time
static uint32_t global_time = 0; // Tracks time since power-on in milliseconds
APP_TIMER_DEF(global_time_timer); // Timer instance
static void global_time_timer_handler(void *p_context);

// Battery ADC pin
#define VBAT_ADC             NRF_SAADC_INPUT_AIN3 // ADC pin for battery voltage measurement, P05/AIN3
static uint16_t read_battery_voltage_mv(void);
static uint64_t read_uLED_check(void);

#define LED_CURRENT_ADC      NRF_SAADC_INPUT_AIN2 // ADC pin for LED current measurement, P04/AIN2

//Mapping to remap AX values to uLED array index
static uint8_t AX_map[8] = {3,7,6,5,2,4,1,0};
static uint8_t AY_map[8] = {5,6,7,4,3,1,0,2};

NRF_BLE_GATT_DEF(m_gatt);
BLE_ADVERTISING_DEF(m_advertising);

// Single timer instance for all timing operations
const nrf_drv_timer_t TIMER_OPTO = NRF_DRV_TIMER_INSTANCE(1);

// PWM instance for LED amplitude control
static nrf_drv_pwm_t m_pwm0 = NRF_DRV_PWM_INSTANCE(0);

static uint16_t m_conn_handle = BLE_CONN_HANDLE_INVALID;

/* I2C IMU + MAG definition */
// TWI/I2C Configuration
#define TWI_SCL_PIN                 28   // Define SCL pin
#define TWI_SDA_PIN                 16   // Define SDA pin
#define TWI_INSTANCE_ID             0


// IIM-42652 IMU Configuration
#define IIM42652_I2C_ADDR          0x68   // 7-bit I2C address (AD0=0)
#define IIM42652_WHO_AM_I_REG      0x75   // WHO_AM_I register

// Add these new definitions in the IMU configuration section
#define IMU_DATA_TIMER_INTERVAL    APP_TIMER_TICKS(1000/imu_sample_rate)  // 100Hz = ~100ms interval
#define IIM42652_GYRO_DATA_REG    0x25    // Gyro data registers
#define IIM42652_ACCEL_DATA_REG   0x1F    // Accel data registers
#define IIM42652_PWR_MGMT0_REG    0x4E    // Power management register
#define IIM42652_GYRO_CONFIG0_REG 0x4F    // Gyro configuration register
#define IIM42652_ACCEL_CONFIG0_REG 0x50   // Accel configuration register

// LIS2MDLTR Magnetometer Configuration
#define LIS2MDLTR_I2C_ADDR      0x1E   // 7-bit I2C address for LIS2MDLTR
#define LIS2MDLTR_OUTX_L_REG    0x68   // Output X low byte register
#define LIS2MDLTR_OUTY_L_REG    0x6A   // Output Y low byte register
#define LIS2MDLTR_OUTZ_L_REG    0x6C   // Output Z low byte register
#define LIS2MDLTR_WHO_AM_I_REG  0x4F   // WHO_AM_I register
#define LIS2MDLTR_WHO_AM_I_VAL  0x40   // Expected value for LIS2MDLTR


// IMU buffer
#define IMU_DATA_BUFFER_SIZE 32
static int16_t imu_data_buffer[IMU_DATA_BUFFER_SIZE][11];
static volatile uint16_t imu_data_buf_head = 0;
static volatile uint16_t imu_data_buf_tail = 0;


// TWI instance
static const nrf_drv_twi_t m_twi = NRF_DRV_TWI_INSTANCE(TWI_INSTANCE_ID);

// Global variables
static bool m_twi_initialized = false;

// Add new timer definition after other APP_TIMER_DEFs
APP_TIMER_DEF(m_imu_timer_id);

// Add new characteristic handles in the handle section
static ble_gatts_char_handles_t m_imu_data_char_handles;
static ble_gatts_char_handles_t m_imu_enable_char_handles;
static ble_gatts_char_handles_t m_imu_sample_rate_char_handles;

// Add these new function prototypes in the forward declarations section
static void imu_timer_handler(void * p_context);
static ret_code_t imu_read_data(void);
static ret_code_t imu_configure(void);
static ret_code_t mag_configure(void);
static void send_next_imu_data(void);
// Temporarily unused, for future use
static ret_code_t i2c_devices_init(void);
static ret_code_t imu_init(void);

// Add new control variables
static bool imu_streaming = false;
static uint32_t imu_samplestamp = 0;

#define I2C_TRANSFER_TIMEOUT_MS 500

// Watchdog configuration
#define WDT_TIMEOUT_MS 5000  // 5 second timeout
static nrfx_wdt_channel_id m_channel_id;

/* End of I2C IMU+MAG definition */


static void advertising_start(bool erase_bonds);

// Stimulation phases
typedef enum {
    STIM_PHASE_INIT,
    STIM_PHASE_RAMP_UP,
    STIM_PHASE_MAIN,
    STIM_PHASE_RAMP_DOWN,
    STIM_PHASE_COMPLETE
} stimulation_phase_t;

// Forward declarations - declare all functions used before they're defined
static void start_next_led(void);
static void start_next_period(void);
static void start_next_sequence(void);
static void start_sequence(uint8_t sequence_index);
static void start_next_phase(void);
static void start_phase(stimulation_phase_t phase);
static void stimulation_complete(void);
static void extract_selected_leds(uint64_t led_selection, volatile uint8_t *led_array, volatile uint8_t *count);
static void timer_event_handler(nrf_timer_event_t event_type, void* p_context);
static uint8_t calculate_ramp_amplitude(uint8_t sequence_index, uint32_t phase_elapsed_us);
static void update_ramp_amplitude(void);
static void trigger_stimulation(void);

// PWM control functions
static void pwm_init(void);
static void pwm_configure_for_sequence(uint8_t sequence_index);
static void pwm_enable(void);
static void pwm_disable(void);

// DFU forward declarations
static void disconnect(uint16_t conn_handle, void * p_context);

// Watchdog forward declarations
static void wdt_event_handler(void);
static void wdt_init(void);


// ===== Custom GATT Services Implementation (embedded directly) =====

#define UUID_DEVICE_INFO_SERVICE         0x1400
#define UUID_OPTO_CONTROL_SERVICE        0x1401
#define UUID_DATA_STREAMING_SERVICE      0x1402

#define UUID_DEVICE_ID_CHAR              0x1500
#define UUID_FIRMWARE_VERSION_CHAR       0x1501
#define UUID_ULED_COLOR_CHAR             0x1503
#define UUID_ULED_CHECK_CHAR             0x1504
#define UUID_BATTERY_VOLTAGE_CHAR        0x1506
#define UUID_STATUS_LED_CHAR             0x1507
#define UUID_SHAM_LED_CHAR               0x1508
#define UUID_DEVICE_LOG_CHAR             0x1509
#define UUID_LAST_STIM_TIME              0x150A

#define UUID_SEQUENCE_LENGTH_CHAR        0x1600
#define UUID_LED_SELECTION_CHAR          0x1601
#define UUID_DURATION_CHAR               0x1602
#define UUID_PERIOD_CHAR                 0x1603
#define UUID_PULSE_WIDTH_CHAR            0x1604
#define UUID_AMPLITUDE_CHAR              0x1605
#define UUID_PWM_FREQ_CHAR               0x1606
#define UUID_RAMP_UP_TIME_CHAR           0x1607
#define UUID_RAMP_DOWN_TIME_CHAR         0x1608
#define UUID_TRIGGER_CHAR                0x1609
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

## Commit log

2025-09-04 Initial commit of version 0.05 hardware design files
    [1_MCU.schdoc, 1_Power and sensors.schdoc, 1_Sheet_1.schdoc, 2_Power.schdoc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]
2025-11-15 Update to the SFN 2025 poster printed version
2026-01-14 Add device assembly protocol, PCBA production files
    [BOM_OptoGrid_Battery_V0.05_OptoGrid_Battery_V0.05_2025-08-04.xlsx, BOM_OptoGrid_Main_V0.05_OptoGrid_Main_V0.05_2025-08-04.xlsx, BOM_OptoGrid_uLEDArray_V0.05_Op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]
2026-01-23 Update assembly SOP
2026-01-23 Update 3D file to V0.051, which optimizes for ease of attachment
    [OptoGrid_V0.051_Assembly.SLDASM, OptoGrid_V0.051_Assembly.STEP, OptoGrid_V0.05_Assembly.SLDASM, OptoGrid_V0.05_Assembly.STEP]
2026-04-18 Added Battery Charger PCBA design and production files
    [BOM_Battery_Charger_V0.05_Battery_Charger_V0.05_2026-01-26.xlsx, PickAndPlace_Battery_Charger_V0.05_2026-01-26.xlsx]
